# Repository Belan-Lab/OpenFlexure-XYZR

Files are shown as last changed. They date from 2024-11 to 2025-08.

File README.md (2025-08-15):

Stand With Ukraine (https://stand-with-ukraine.pp.ua)

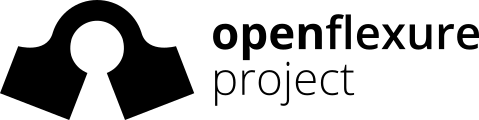
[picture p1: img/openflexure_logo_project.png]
OpenFlexure Project (https://gitlab.com/openflexure)


OpenFlexure Block Stage for SPIM
============================

Fork of [OpenFlexure Block Stage](https://gitlab.com/openflexure/openflexure-block-stage/) project.

Modification of the original Block Stage for SPIM imaging.

Department of Molecular Biophysics, Bogomoletz Institute of Physiology of NAS of Ukraine (Kyiv, Ukraine).

---

# Setup overview

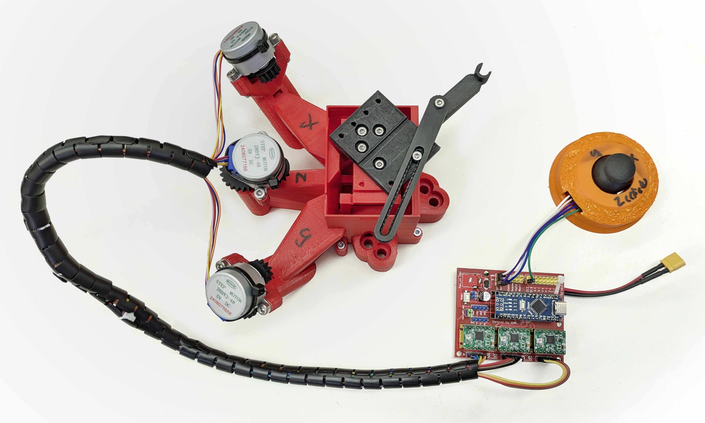
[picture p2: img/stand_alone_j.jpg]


Part|#|Cost/unit|Link
-|-|-|-
OpenFlexure Block Stage | 1x | $11 |-
Arduino Nano compatible board | 1x | $2.13 | [AliExpress](https://a.aliexpress.com/_EwrjzyD) 
Arduino Nano CNC board | 1x | $2.8 | [arduino.ua](https://arduino.ua/prod1745-modyl-3d-printera-v-3-0) 
Stepper driver A4988 | 3x | $1.3 | [arduino.ua](https://arduino.ua/prod965-draiver-shagovogo-dvigatelya-stepstick-a4988) 
Stepper drive 28BYJ-48, 5V | 3x | $1.45 | [arduino.ua](https://arduino.ua/prod216-shagovii-dvigatel-5v-28byj-48) 
Joystick module | 1x | $0.75 | [arduino.ua](https://arduino.ua/prod194-djoistik-dlya-arduino) 
Mini560 Pro Step Down to 5V | 1x | $0.85 | [AliExpress](https://a.aliexpress.com/_EJQFP5x) 
XT30 connector | 1x | $0.6 | [arduino.ua](https://arduino.ua/prod5276-xt30-konnektor-para-dlya-podklucheniya-li-po-li-ion-akkymylyatorov) 
30 cm Dupont jumpers kit | 1x | $0.95 | [arduino.ua](https://arduino.ua/prod2334-pepermichki-mama-papa-300mm) 
10 mm Spiral cable organizer | 1x | $2.60 | [AliExpress](https://a.aliexpress.com/_EIXyu5w) 
__Total__ |  | __~$30__ |

# Travel distances enlargement
## Modification V0
The original OpenFlexure Block stage has only ~2 mm travel distances in each direction, which is not enough for large sample imaging. So, due to the parametric nature of the OpenFlexure Block Stage model, I just adjusted several variables in the `parameters.scad` file to obtain an STL model of the stage with enlarged travel distances.  Additionally, I established a new variable `platform_z_add` which was just a constant in `platform_z` calculation (line 80) to control base high.

I am listing the changed parameters below:

| Variable               | Original value | Adjusted value |
| ---------------------- | -------------- | -------------- |
| `beam_height`          | 75             | 100            |
| `stage_to_beam_height` | 12.5           | 0              |
| `xy_lever`             | 10             | 30             |
| `flex_a`               | 0.1            | 0.2            |
| `platform_z_add`       | 7              | 20             |

Sample movement parameters:
- `xy_reduction`=  50 / `xy_lever` = 50/30 = 1.6
- `z_reducion` =  50 / `z_lever` = 50/10 = 5
- M3 screw pitch 0.5 mm

With selected parameters, we achieve next characteristics:

| Axis | Travel distance | Travel per screw revolution (estimated) |
| ---- | --------------- | --------------------------------------- |
| X    | ~6 mm           | 0.313 mm                                |
| Y    | ~6 mm           | 0.313 mm                                |
| Z    | ~3 mm           | 0.1 mm                                  |

__Materials:__

| Part                 | #      | Cost/unit | Link                                                         |
| -------------------- | ------ | --------- | ------------------------------------------------------------ |
| 1.75 mm PLA filament | ~200 g | ~$4.75    | [Monofilament](https://monofilament.com.ua/ua/products/standartnye-materialy/pla/pla-cvetlo-seryj-o1-75mm-ves0-75kg) |
| Silicone O-ring kit  | 1x     | $4.05     | [AliExpress](https://a.aliexpress.com/_EQdsBUy)              |
| 35 mm M3 screw       | 3x     | ~$0.5     | Metalvis                                                     |
| M3 nut               | 6x     | ~$0.25    | Metalvis                                                     |
| __Total__            |        | __~$11__  |                                                              |

# Setup configurations
## Stand-alone joystick control
Simple single speed stage control with joystick, sketch `arduino/cnc_board_joystick_xyz.ino`. Stage works in two modes, XY movement and Z movement, switching between them with joystick click button.

Stepper speed set up at 15 RPM, which achiwed travel speed 0.08 mm/s for XY axes and 0.025 mm/s for Z axis. Minimum rotation value set at 10 degrees per joystick activation. 

Estimated movement parameters:
- ~9 um per joystick activation for XY axes 
- ~3 um per joystick activation for Z axis

[Joystick module case](https://www.printables.com/model/653949-joystick-module-case) model avaliables on Printables (© @ZbychuM_510985).

## μManager control
3-axis stage control with [MarzhauserLStep](https://micro-manager.org/MarzhauserLStep) device adapter, Inspired by [CustomArduino](https://micro-manager.org/CustomArduino) vLStep Z-Axis solution.

# Hardware modifications
## Simple sample holder
Good practice for sample fixation during SPIM imaging is embedding the sample in agarose gel. 1 ml syringes are very suitable for large samples, so I designed a "lego figure hand"-like holder for a standard 1 ml insulin syringe. 

> [!TIP]
>
> Read about [sample preparation for SPIM](https://openspim.org/Sample_Preparation).

 Sample holder model V0 | Block Stage top view   | Block Stage side view 
:-------------------------:|:-------------------------:|:-------------------------:
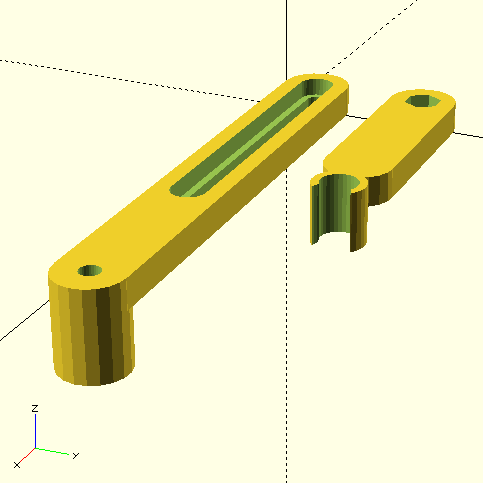
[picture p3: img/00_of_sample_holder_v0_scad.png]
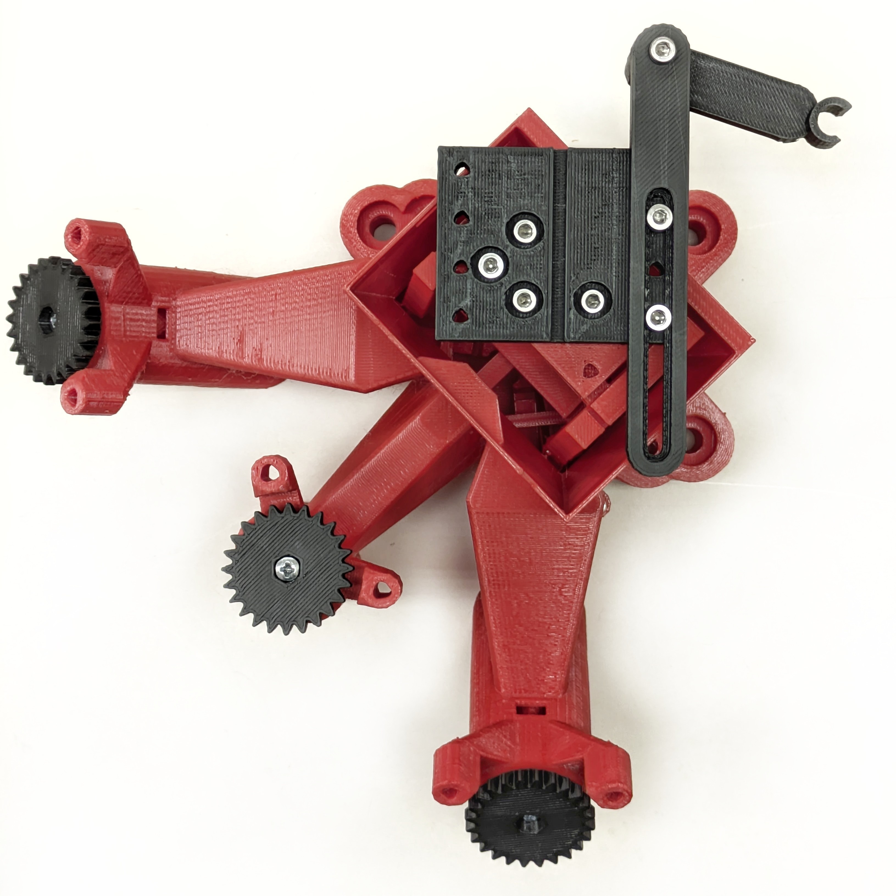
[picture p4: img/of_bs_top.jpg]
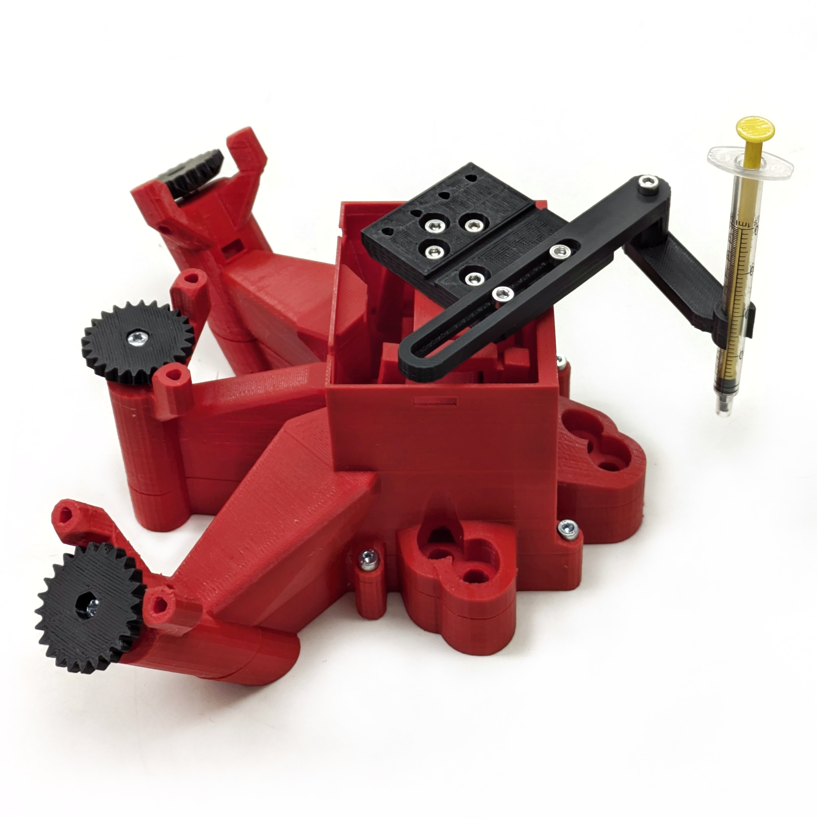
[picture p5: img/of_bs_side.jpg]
||

## R-axis arm
Moving platform modification with additional rotary axis.

_in progress_

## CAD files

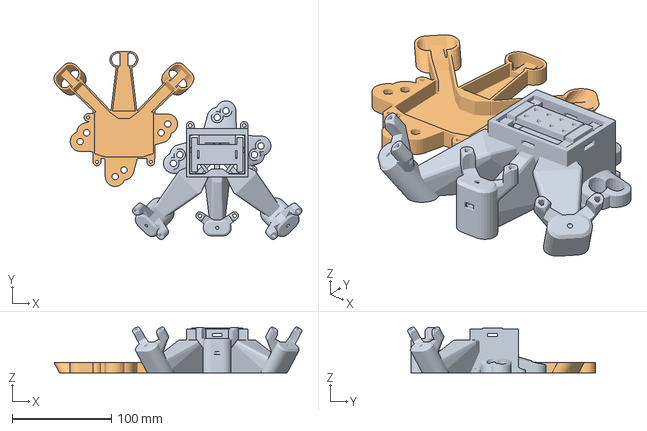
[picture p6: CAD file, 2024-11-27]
models/block_stage_large/K1/main_body_00.3mf
249.4 x 188.9 x 46.1 mm
main_body.stl
base.stl

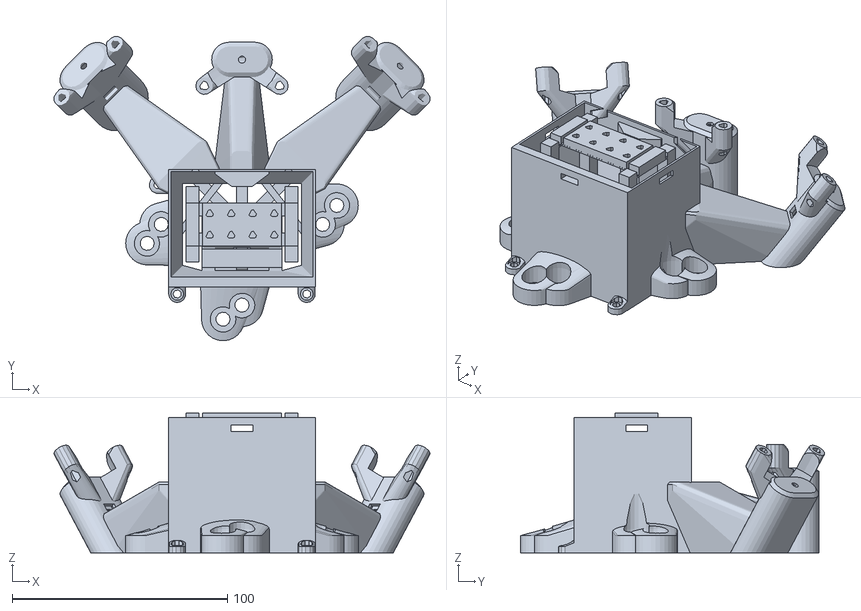
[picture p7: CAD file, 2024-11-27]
models/block_stage_large/builds/main_body.stl
174.8 x 141.4 x 65.0

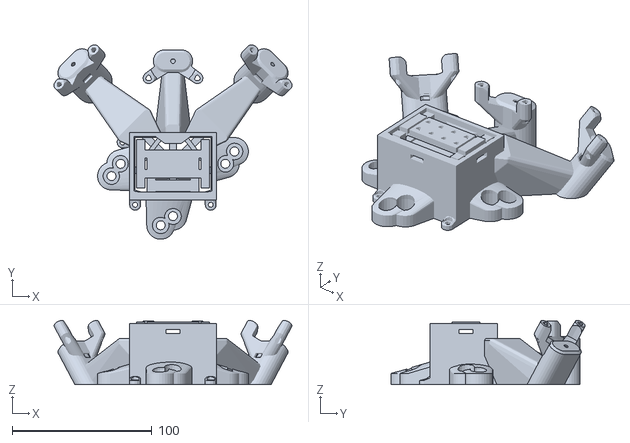
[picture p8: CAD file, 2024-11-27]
models/block_stage_original/builds/main_body.stl
170.5 x 139.3 x 46.1

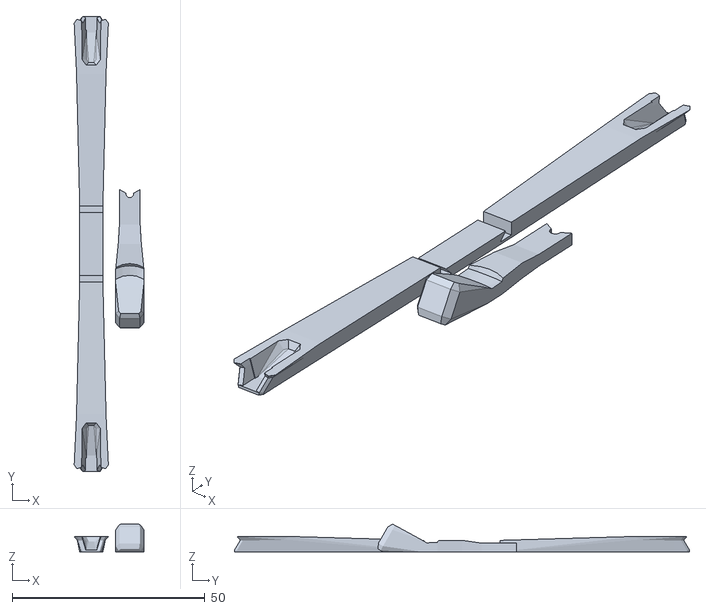
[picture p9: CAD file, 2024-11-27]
models/block_stage_original/builds/actuator_assembly_tools.stl
18.1 x 118.2 x 7.23

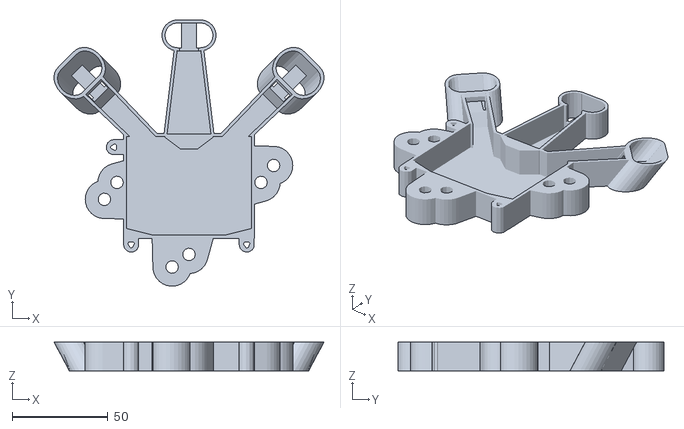
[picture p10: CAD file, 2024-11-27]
models/block_stage_large/builds/base.stl
140.6 x 138.7 x 15.0

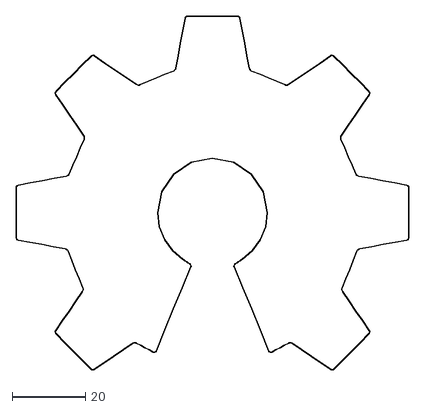
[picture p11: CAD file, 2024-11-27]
models/block_stage_large/openscad/oshw_gear.dxf
107.1 x 96.4

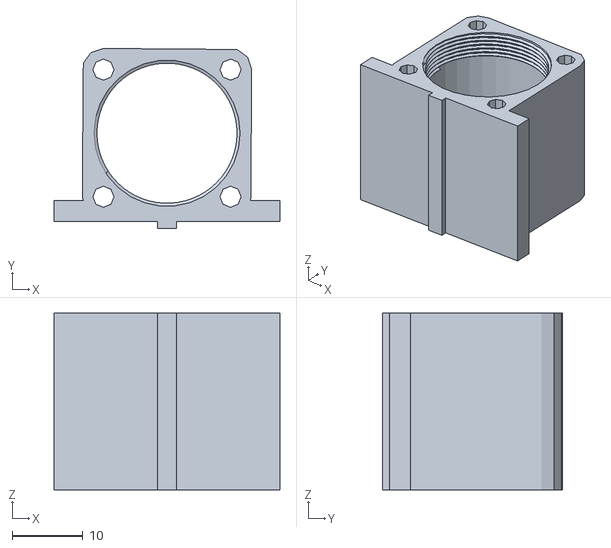
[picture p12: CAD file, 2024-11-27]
models/block_stage_original/builds/accessories/rms_to_top_plate.stl
32.0 x 25.5 x 25.0

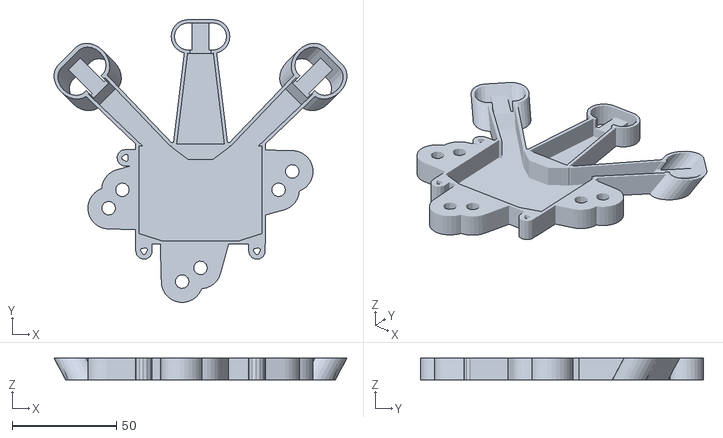
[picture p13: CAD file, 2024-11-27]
models/block_stage_original/builds/base.stl
140.6 x 135.7 x 10.5

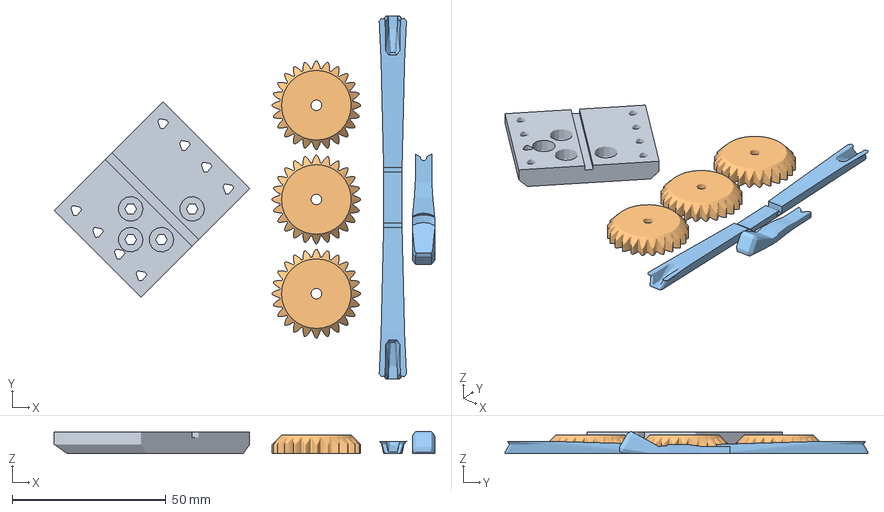
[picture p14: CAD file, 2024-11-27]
models/block_stage_large/K1/moving_platform_00.3mf
123.9 x 118.2 x 7.23 mm
moving_platform.stl
gears.stl
actuator_assembly_tools.stl

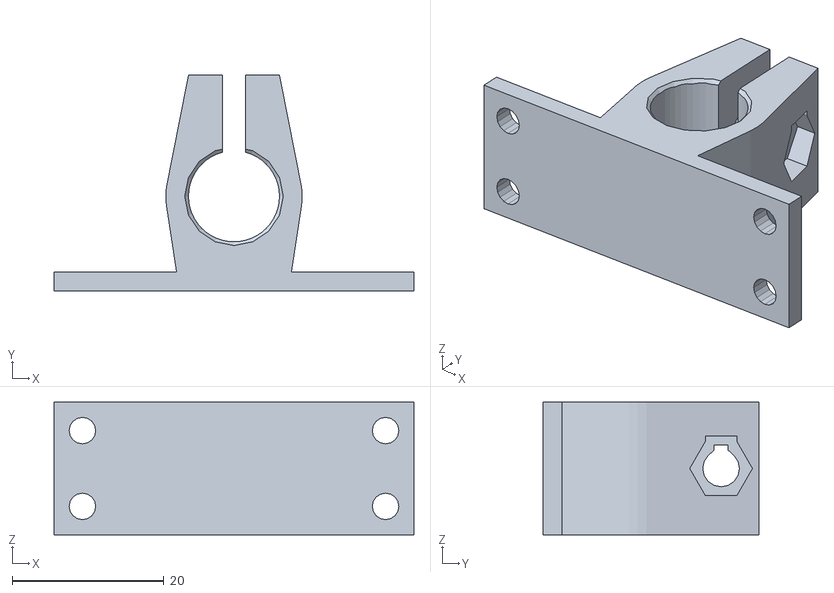
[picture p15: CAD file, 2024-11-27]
models/block_stage_original/builds/accessories/CPS532_to_top_plate.stl
47.5 x 28.5 x 17.5

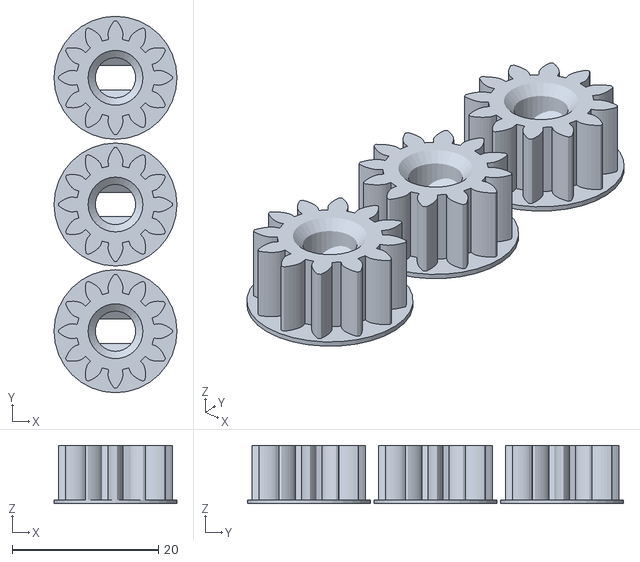
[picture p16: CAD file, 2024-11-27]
models/block_stage_original/builds/small_gears.stl
16.8 x 51.5 x 8.00

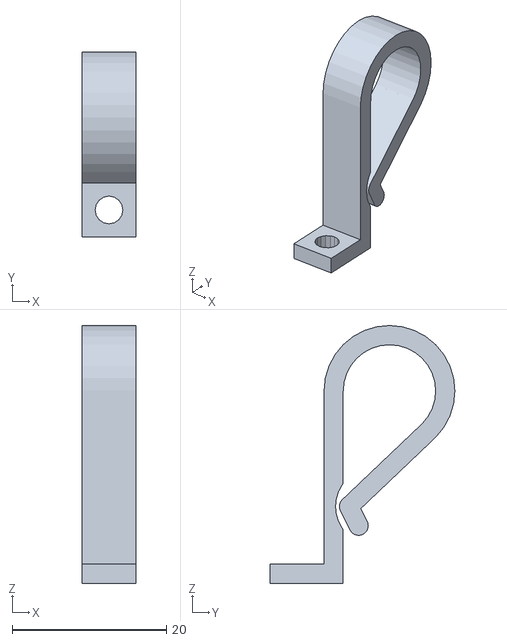
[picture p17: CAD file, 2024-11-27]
models/block_stage_original/builds/accessories/vertical_sample_clips.stl
7.00 x 24.0 x 33.5

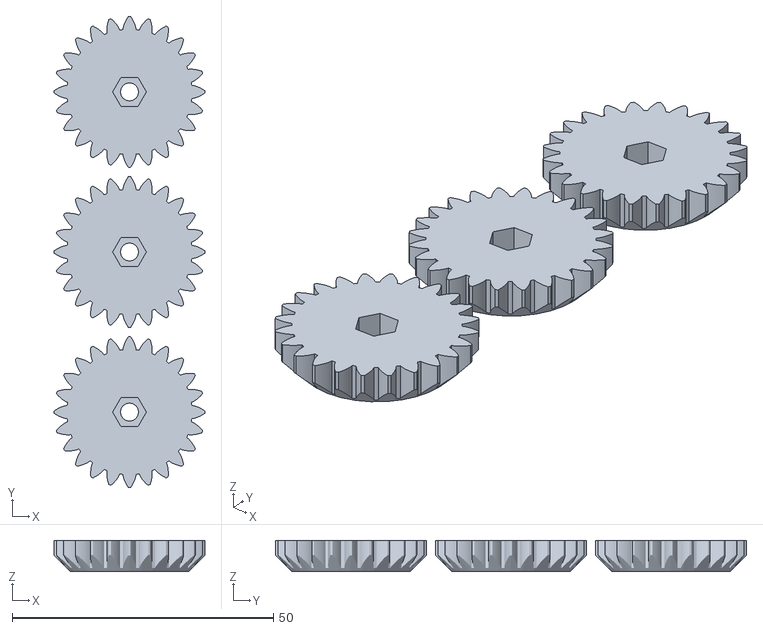
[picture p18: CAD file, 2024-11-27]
models/block_stage_original/builds/gears.stl
28.9 x 90.2 x 6.00

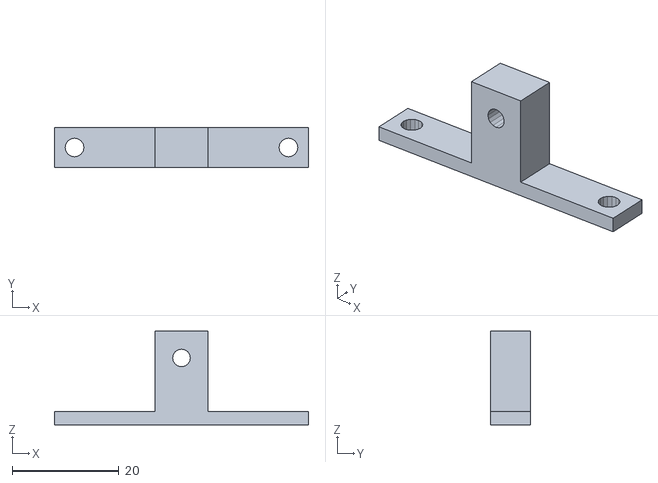
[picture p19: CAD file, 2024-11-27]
models/block_stage_original/builds/accessories/LED_to_top_plate.stl
47.5 x 7.50 x 17.5

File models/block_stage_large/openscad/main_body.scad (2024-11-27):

use <utilities.scad>;
use <compact_nut_seat.scad>;
use <fibre_stage_three_legs.scad>;
include <parameters.scad>;

module exterior_brim(r=4, h=0.2){
    // Add a "brim" around the outside of an object *only*, preserving holes in the object
    children();
    
    if(r>0) linear_extrude(h) difference(){
        offset(r) projection(cut=true) translate([0,0,-d]) children();
       
        offset(-r) offset(r) projection(cut=true) translate([0,0,-d]) children();
    }
}
module z_base(){
    // Trapezoid that forms the base of the Z stage
    t = xy_bottom_travel;
    w = z_stage_base_w;
    hull(){
        translate([-pw,-pw-t,0]) cube([2*pw,d,d]); // inner edge
        translate([-w/2, -stage[1]/2-t, 0]) cube([w, d, d]);
        translate([-w/2, z_stage_base_y, 0]) cube([w, d, d]);
    }
}

module z_stage(){
    // This is the part that moves in Z only, connected to the middle
    // "shelf" of the XY table
    // The triangular base of this part must fit between the 
    // pushsticks for the XY motion, which constrains the tip position
    // and also means we must bring the sides out at 45 degrees.
    difference(){
        sequential_hull(){
            z_base();
            translate([0,0,stage[2]]) z_base();
            translate([0,0,shelf_z1 + stage[2]/2]) cube(stage,center=true);
        }
        
        // clearance for Z pushstick (see below)
        translate([-pw/2-1.5, -99, z_pushstick_z - 2 - z_travel]){
            cube([pw+3, 999, pushstick[2]+3.5+2*z_travel]);
        }
    }
    // Join the stage to the anchor with some flexures at the bottom
    reflect([1,0,0]) translate([-z_stage_base_w/2,z_anchor_bottom_y-d,0])
        cube([zflex[0], z_lever + zflex[1]+2*d, zflex[2]]);
    translate([-z_stage_base_w/2,z_anchor_bottom_y+zflex[1],0])
        cube([z_stage_base_w, z_lever - zflex[1], pushstick[2]]);
    // And more flexures at the top
    reflect([1,0,0]) translate([-stage[0]/2,-stage[1]/2,shelf_z1]) mirror([0,1,0]){
        translate([0,-d,0]) cube([zflex[0], z_lever + zflex[1]+2*d, zflex[2]]);
        translate([0,zflex[1],dz]) cube([stage[0]/2+d,z_lever - zflex[1], stage[2]-dz]);
    }
    // The actuating "pushstick" attaches to this lever
    hull(){
        translate([-pw/2, z_stage_base_y - z_lever, 0]) cube([pw, z_lever - zflex[1], stage[2]]);
        translate([-pw/2, z_stage_base_y - 3 - zflex[1], 0]) cube([pw, 3, shelf_z1 - 3]);
    }
    // This is the actuating "pushstick"
    translate([-pw/2, z_stage_base_y, z_pushstick_z]){
        l = z_actuator_pivot_y - z_stage_base_y;
        cube([pw, l, pushstick[2]]);
        translate([0,-zflex[1]*2,0]) cube([pw, l + 4*zflex[1], zflex[2]]);
    }
}

// Overall structure
module main_body(){
    difference(){
        xy_table();
        
        // cutouts for pushsticks
        each_pushstick() hull() {
            h=stage[2]*2+z_travel*2;
            translate([0,2*d,0]) cube([pw, d, h], center=true);
            translate([0,0.5,0]) cube([pw+1.5, d, h], center=true);
            translate([0, pushstick[1], 0]) cube([pw+1+2*xy_bottom_travel*sqrt(2), d, h], center=true);
            translate([0, pushstick[1], 0]) cube([d, d, h + pw+1+2*xy_bottom_travel*sqrt(2)], center=true);
            translate([99, 98, 0]) cube([d, d, h + pw+1+2*xy_bottom_travel*sqrt(2)], center=true); //cut out between the pushsticks
        }
        
        // cutout for Z stage
        hull(){
            h=stage[2]*2+z_travel*2;
            w = stage[0] - 2*zflex[1];
            translate([0, -pw, 0]) cube([2*pw,d,h],center=true);
            translate([0, -stage[1]/2, 0]) cube([w,2*d,h],center=true);
        }
        
        // mounting holes on top
        repeat([10,0,0],4,center=true)
            repeat([0,10,0],2,center=true)
            translate([0,0,shelf_z2 + 1.5]) trylinder_selftap(3,h=999);
            // NB the z position must clear the bottom of the stage
            // (which is 1mm above shelf_z2) or we get errors on the
            // bridge.
    }
    // XY pushsticks and actuators
    each_pushstick(){
        pushstick();
        translate([0,pushstick[1] - zflex[1],0]) tilted_actuator(shelf_z1, xy_actuator_pivot_w, xy_lever * xy_reduction, base_w = pw);
    }
    
    // Z stage (the part that moves only in Z) and actuator
    z_stage();
    translate([0,z_actuator_pivot_y,0]){
        untilted_actuator(z_pushstick_z, z_actuator_pivot_w, z_lever * z_reduction);
    }
    //reinforcement through the void in the centre
    reflect([1,0,0]) translate([0,0,pushstick[2] + 4 + z_travel]) hull(){
        translate([pw/2+3, z_actuator_pivot_y - wall_t, 0]) cube([4,d,4]);
        translate([stage[0]/2 + zflex[0] + zflex[1] + xy_bottom_travel, -stage[1]/2,0]) cube([0.5,4,4]);
    }
    
    // Casing (also provides a lot of the structural integrity)
    casing();
    // if(fixed_platform) fixed_platform(); <<<<<<<<<<<<<<<<<<
        
    
}//*/
brim_r=0;
exterior_brim(r=brim_r) main_body();

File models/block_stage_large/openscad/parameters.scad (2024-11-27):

/*
  Useful settings/parameters for the OpenFlexure fibre stage
*/
version_numstring = "0.2.1";
stage = [37,20,5]; // dimensions of stage part
beam_height = 100; // 75 <<<<<< height of beam above the table
stage_to_beam_height = 0; // 12.5 <<<<<<
stage_height = beam_height - stage_to_beam_height; //bottom of base to top surface of the stage 
 // NB platform_z sets the distance from bottom of the body to top of the stage
 // stage_height determines the thickness of the base.
platform_z_add = 20;

brim_r = 0;

// Range of travel is lever length * flex_a
xy_lever = 30;  // 10 <<<<<<<<<<<<<<<<<<<<<
z_lever = 10;   // 10 <<<<<<<<<<<<<<<<<<<<<

// Mechanical reduction settings
xy_stage_reduction = 30/xy_lever; //ratio of sample motion to lower shelf motion
xy_reduction = 50/xy_lever; //mechanical reduction from screw to sample
z_reduction = 50/z_lever; //mechanical reduction for Z

// Motor lugs
motor_lugs = true;

// fixed platform for fibre launch
//fixed_platform = false; // this is overwritten later on with the dimensions anyway.

// Mounting holes
breadboard_lugs="diagonal"; //sets the hole pattern for bolting it down.  See the options below.

// Flexure dimensions - good for PLA and ~0.5mm nozzle
zflex = [6, 1.5, 0.75]; //dimensions of flexure
xflex = [5,5.5,5]; //default bounding box of x flexure
xflex_t = 1; //thickness of bendy bit in x
flex_a = 0.2; //angle through which flexures are bent, radians, 0.1 <<<<<
dz = 0.5; //thickness before a bridge is printable-on

xy_travel = xy_lever * flex_a; //max. travel in X or Y
xy_bottom_travel = xy_travel * xy_stage_reduction; //travel of bottom of XY stage
xy_actuator_pivot_w = 25; //width of the hinge for the actuating lever
actuator_h = 26; //height of actuator columns (~screw length)

pushstick = [5,38,5]; //cross-section of XY "push stick"
pw = pushstick[0]; //because this is used in a lot of places...

wall_t = 1.6;
d=0.05;

// Height of the bridging "shelves" in the XY axis "table" structure
shelf_z1 = xy_lever * xy_stage_reduction;
shelf_z2 = shelf_z1 + xy_lever;

// Z axis geometry
z_travel = z_lever * flex_a; //max. travel in Z
z_stage_base_y = -stage[1]/2-xy_bottom_travel; //position of the flexure edge of the Z stage
z_stage_base_w = stage[0] + 2*zflex[1] - 2*xy_bottom_travel - 2; //width of the flexure edge of the Z stage
z_anchor_bottom_y = z_stage_base_y - z_lever - zflex[1]; // lower Z stage end of the fixed base
z_actuator_pivot_y = stage[1]/2 + zflex[1] + zflex[0] + xy_bottom_travel + wall_t;
z_actuator_pivot_w = 20; //width of the hinge for the Z actuator lever
z_pushstick_z = shelf_z1 - pw - 2.5; // height of the Z pushstick

// Mounting stuff
// By default, place 3 mounting holes to align the centre of the stage with a hole.
// setting beam_between_holes adds another set of holes, putting the beam halfway between
bolt_spacing = 25; // change to 25.4 for imperial tables
mounting_bolts_alongholes = [[-1,0,0],[0,-1,0],[1,0,0]]*1.5*bolt_spacing; //beam aligned with holes
mounting_bolts_betweenholes = [[-1.25,-0.25,0],[1.25,0.25,0],[-0.25,-1.25,0]]*1.41*bolt_spacing;
mounting_bolts_atsides = [[-1.5,0,0],[1.5,0,0],[-1.5,-1,0],[1.5,-1,0]] * bolt_spacing;
mounting_bolts_diagonal = concat(mounting_bolts_alongholes, 
                                 mounting_bolts_betweenholes);
// I hope you'll excuse the stacked ternaries, this is an unpleasant necessity :(
mounting_bolts = breadboard_lugs=="atsides"?mounting_bolts_sides:
                 breadboard_lugs=="diagonal"?mounting_bolts_diagonal:
                 breadboard_lugs=="alongholes"?mounting_bolts_alongholes:
                 breadboard_lugs=="betweenholes"?mounting_bolts_betweenholes:
                 /*breadboard_lugs=="none"?*/[];
            
platform_z = shelf_z2 + stage[2] + platform_z_add; // 7 <<<<<<< The platform is a fixed height above the moving stage
fixed_platform_standoff = 10;
fixed_platform = [50,40,4];
platform_gap = xy_travel + 1;

//term for calculating casing size
casing_size_s = xy_bottom_travel + zflex[1] + zflex[0] + 0.5 + wall_t;
//casing size
casing_size = stage + [2*casing_size_s,casing_size_s + (-z_anchor_bottom_y-stage[1]/2) + wall_t,shelf_z2];
casing_top = shelf_z2 + stage[2] - z_travel; // top of the wall
max_actuator_travel = max(xy_travel*xy_reduction, z_travel*z_reduction); // maximum distance the actuators protrude below the stage
echo(max_actuator_travel);

base_height = stage_height - platform_z; // the base takes up any height not use by the body.
if(base_height < max_actuator_travel + 4) echo("WARNING: stage_height is too low, base will not compile properly!");

//foot_height is required for the actuator assembly tools
foot_height = 20;

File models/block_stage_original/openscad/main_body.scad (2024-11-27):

use <utilities.scad>;
use <compact_nut_seat.scad>;
use <fibre_stage_three_legs.scad>;
include <parameters.scad>;

module exterior_brim(r=4, h=0.2){
    // Add a "brim" around the outside of an object *only*, preserving holes in the object
    children();
    
    if(r>0) linear_extrude(h) difference(){
        offset(r) projection(cut=true) translate([0,0,-d]) children();
       
        offset(-r) offset(r) projection(cut=true) translate([0,0,-d]) children();
    }
}
module z_base(){
    // Trapezoid that forms the base of the Z stage
    t = xy_bottom_travel;
    w = z_stage_base_w;
    hull(){
        translate([-pw,-pw-t,0]) cube([2*pw,d,d]); // inner edge
        translate([-w/2, -stage[1]/2-t, 0]) cube([w, d, d]);
        translate([-w/2, z_stage_base_y, 0]) cube([w, d, d]);
    }
}

module z_stage(){
    // This is the part that moves in Z only, connected to the middle
    // "shelf" of the XY table
    // The triangular base of this part must fit between the 
    // pushsticks for the XY motion, which constrains the tip position
    // and also means we must bring the sides out at 45 degrees.
    difference(){
        sequential_hull(){
            z_base();
            translate([0,0,stage[2]]) z_base();
            translate([0,0,shelf_z1 + stage[2]/2]) cube(stage,center=true);
        }
        
        // clearance for Z pushstick (see below)
        translate([-pw/2-1.5, -99, z_pushstick_z - 2 - z_travel]){
            cube([pw+3, 999, pushstick[2]+3.5+2*z_travel]);
        }
    }
    // Join the stage to the anchor with some flexures at the bottom
    reflect([1,0,0]) translate([-z_stage_base_w/2,z_anchor_bottom_y-d,0])
        cube([zflex[0], z_lever + zflex[1]+2*d, zflex[2]]);
    translate([-z_stage_base_w/2,z_anchor_bottom_y+zflex[1],0])
        cube([z_stage_base_w, z_lever - zflex[1], pushstick[2]]);
    // And more flexures at the top
    reflect([1,0,0]) translate([-stage[0]/2,-stage[1]/2,shelf_z1]) mirror([0,1,0]){
        translate([0,-d,0]) cube([zflex[0], z_lever + zflex[1]+2*d, zflex[2]]);
        translate([0,zflex[1],dz]) cube([stage[0]/2+d,z_lever - zflex[1], stage[2]-dz]);
    }
    // The actuating "pushstick" attaches to this lever
    hull(){
        translate([-pw/2, z_stage_base_y - z_lever, 0]) cube([pw, z_lever - zflex[1], stage[2]]);
        translate([-pw/2, z_stage_base_y - 3 - zflex[1], 0]) cube([pw, 3, shelf_z1 - 3]);
    }
    // This is the actuating "pushstick"
    translate([-pw/2, z_stage_base_y, z_pushstick_z]){
        l = z_actuator_pivot_y - z_stage_base_y;
        cube([pw, l, pushstick[2]]);
        translate([0,-zflex[1]*2,0]) cube([pw, l + 4*zflex[1], zflex[2]]);
    }
}

// Overall structure
module main_body(){
    difference(){
        xy_table();
        
        // cutouts for pushsticks
        each_pushstick() hull() {
            h=stage[2]*2+z_travel*2;
            translate([0,2*d,0]) cube([pw, d, h], center=true);
            translate([0,0.5,0]) cube([pw+1.5, d, h], center=true);
            translate([0, pushstick[1], 0]) cube([pw+1+2*xy_bottom_travel*sqrt(2), d, h], center=true);
            translate([0, pushstick[1], 0]) cube([d, d, h + pw+1+2*xy_bottom_travel*sqrt(2)], center=true);
            translate([99, 98, 0]) cube([d, d, h + pw+1+2*xy_bottom_travel*sqrt(2)], center=true); //cut out between the pushsticks
        }
        
        // cutout for Z stage
        hull(){
            h=stage[2]*2+z_travel*2;
            w = stage[0] - 2*zflex[1];
            translate([0, -pw, 0]) cube([2*pw,d,h],center=true);
            translate([0, -stage[1]/2, 0]) cube([w,2*d,h],center=true);
        }
        
        // mounting holes on top
        repeat([10,0,0],4,center=true)
            repeat([0,10,0],2,center=true)
            translate([0,0,shelf_z2 + 1.5]) trylinder_selftap(3,h=999);
            // NB the z position must clear the bottom of the stage
            // (which is 1mm above shelf_z2) or we get errors on the
            // bridge.
    }
    // XY pushsticks and actuators
    each_pushstick(){
        pushstick();
        translate([0,pushstick[1] - zflex[1],0]) tilted_actuator(shelf_z1, xy_actuator_pivot_w, xy_lever * xy_reduction, base_w = pw);
    }
    
    // Z stage (the part that moves only in Z) and actuator
    z_stage();
    translate([0,z_actuator_pivot_y,0]){
        untilted_actuator(z_pushstick_z, z_actuator_pivot_w, z_lever * z_reduction);
    }
    //reinforcement through the void in the centre
    reflect([1,0,0]) translate([0,0,pushstick[2] + 4 + z_travel]) hull(){
        translate([pw/2+3, z_actuator_pivot_y - wall_t, 0]) cube([4,d,4]);
        translate([stage[0]/2 + zflex[0] + zflex[1] + xy_bottom_travel, -stage[1]/2,0]) cube([0.5,4,4]);
    }
    
    // Casing (also provides a lot of the structural integrity)
    casing();
    // if(fixed_platform) fixed_platform(); <<<<<<<<<<<<<<<<<<
        
    
}//*/
brim_r=0;
exterior_brim(r=brim_r) main_body();

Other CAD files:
models/block_stage_original/builds/moving_platform.stl
models/block_stage_original/openscad/parameters.scad
models/block_stage_large/openscad/accessories/CPS532_to_top_plate.scad
models/block_stage_large/openscad/accessories/LED_to_top_plate.scad
models/block_stage_large/openscad/accessories/cylinder_clamp.scad
models/block_stage_large/openscad/accessories/microscope_module.scad
models/block_stage_large/openscad/accessories/microscope_module_infiniteconjugates.scad
models/block_stage_large/openscad/accessories/optics_module_rms_f50d13_nodovetail.scad
models/block_stage_large/openscad/accessories/optics_mounts.scad
models/block_stage_large/openscad/accessories/picamera_shim.scad
models/block_stage_large/openscad/accessories/rms_to_top_plate.scad
models/block_stage_large/openscad/accessories/thorlabs_threads.scad
models/block_stage_large/openscad/accessories/vertical_sample_clips.scad
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

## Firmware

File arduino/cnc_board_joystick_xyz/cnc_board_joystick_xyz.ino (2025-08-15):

// Nano CNC board with stepper lib and joystick control

// #include "A4988.h"
#include <Arduino.h>
#include "BasicStepperDriver.h"
#include "MultiDriver.h"
#include "SyncDriver.h"

// joystick set up
#define X_STICK A7
#define Y_STICK A6
#define J_CLICK 12

#define U_LIM 614
#define D_LIM 414

int xPos = 0;
int yPos = 0;
int bStt = 0;
int bSttLast = 0;
int bPress = 0;

// steppers set up
#define X_DIR 2          // X-axis dir pin   X-2, Y-3. Z-4 
#define X_STEP 5         // X-axis step pin  X-5, Y-6. Z-7 


#define Y_DIR 3          // y-axis dir pin   X-2, Y-3. Z-4 
#define Y_STEP 6         // Y-axis step pin  X-5, Y-6. Z-7 


#define Z_DIR 4          // z-axis dir pin   X-2, Y-3. Z-4 
#define Z_STEP 7         // Z-axis step pin  X-5, Y-6. Z-7 


#define MOTOR_EN 8       // drivers enable pin

#define MOTOR_STEPS 2047  // steps per revolution

BasicStepperDriver stepperX(MOTOR_STEPS, X_DIR, X_STEP);
BasicStepperDriver stepperY(MOTOR_STEPS, Y_DIR, Y_STEP);
BasicStepperDriver stepperZ(MOTOR_STEPS, Z_DIR, Z_STEP);

SyncDriver controller(stepperX, stepperY, stepperZ);

int rotate = 360;


void setup() {
  // initialize serial communications at 9600 bps:
  Serial.begin(9600); 
  
  pinMode(X_STICK, INPUT);
  pinMode(Y_STICK, INPUT);
  pinMode(J_CLICK, INPUT_PULLUP);

  pinMode(MOTOR_EN, OUTPUT);
  digitalWrite(MOTOR_EN, LOW);

  stepperX.begin(15., 1);
  stepperY.begin(15., 1);
  stepperZ.begin(15., 1);

  pinMode(MOTOR_EN, OUTPUT);
  digitalWrite(MOTOR_EN, HIGH);

}


void loop() {
  bState();

  xPos = analogRead(X_STICK);
  yPos = analogRead(Y_STICK);
  
  if (bPress == 0){
    xyMove();
  }
  else if (bPress == 1){
    zMove();
  }

  Serial.print("X: ");
  Serial.print(xPos);
  Serial.print(" | Y: ");
  Serial.print(yPos);
  Serial.print(" | Button: ");
  Serial.println(bPress);
}


void xyMove() {
  if ((xPos > U_LIM) && (yPos > U_LIM)){
    digitalWrite(MOTOR_EN, LOW);
    delayMicroseconds(10);
    controller.rotate(-10, 10, 0);
    }
  else if ((xPos < D_LIM) && (yPos < D_LIM)){
    digitalWrite(MOTOR_EN, LOW);
    delayMicroseconds(10);
    controller.rotate(10, -10, 0);
    }
  else if ((xPos < D_LIM) && (yPos > U_LIM)){
    digitalWrite(MOTOR_EN, LOW);
    delayMicroseconds(10);
    controller.rotate(10, 10, 0);
    }
  else if ((xPos > U_LIM) && (yPos < D_LIM)){
    digitalWrite(MOTOR_EN, LOW);
    delayMicroseconds(10);
    controller.rotate(-10, -10, 0);
    }
  else if (yPos < D_LIM){
    digitalWrite(MOTOR_EN, LOW);
    delayMicroseconds(10);
    controller.rotate(0, -10, 0);
    }
  else if (yPos > U_LIM){
    digitalWrite(MOTOR_EN, LOW);
    delayMicroseconds(10);
    controller.rotate(0, 10, 0);
    }
  else if (xPos < D_LIM){
    digitalWrite(MOTOR_EN, LOW);
    delayMicroseconds(10);
    controller.rotate(10, 0, 0);
    }
  else if (xPos > U_LIM){
    digitalWrite(MOTOR_EN, LOW);
    delayMicroseconds(10);
    controller.rotate(-10, 0, 0);
    }
}


void zMove() {
  if (yPos < D_LIM){
    digitalWrite(MOTOR_EN, LOW);
    delayMicroseconds(10);
    controller.rotate(0, 0, 10);
    }
  else if (yPos > U_LIM){
    digitalWrite(MOTOR_EN, LOW);
    delayMicroseconds(10);
    controller.rotate(0, 0, -10);
    }
}


void bState() {
  int bStt = digitalRead(J_CLICK);

  if (bStt == LOW && bSttLast == HIGH) {
    bPress = !bPress;
  }

  bSttLast = bStt;
}

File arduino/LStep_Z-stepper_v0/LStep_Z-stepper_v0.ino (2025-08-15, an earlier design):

// Modified Arduino firmware for A4988 stepper and Micro-Manager compatibility
// Non-blocking stepper control with proper status reporting
// Stand-alone stepper control

// Motor configuration
#define MOTOR_STEPS 200     // Steps per revolution
#define MICROSTEPS 1        // Microstepping

// Pin definitions for A4988
#define DIR_PIN 4
#define STEP_PIN 7
#define ENABLE_PIN 8

String cmd = "";
float z = 0.0;
long stepPosition = 0;        // Current position in steps
float stepsPerUnit = 100.0;   // Steps per micrometer (adjust for your setup)

// Non-blocking movement variables
bool isMoving = false;
long moveStepsRemaining = 0;
int moveDirection = 1;
unsigned long lastStepTime = 0;
unsigned long stepIntervalMicros = 5000; // Default: 200 steps/sec

void setup() {
  Serial.begin(9600);
  
  // Configure stepper pins
  pinMode(DIR_PIN, OUTPUT);
  pinMode(STEP_PIN, OUTPUT);
  pinMode(ENABLE_PIN, OUTPUT);
  digitalWrite(ENABLE_PIN, LOW); // Enable motor (LOW = enabled for A4988)
  
  delay(1000);
  
  reply("Vers:LS");
}

void loop() {
  // Handle serial commands - HIGHEST PRIORITY
  if (Serial.available()) {
    cmd = Serial.readStringUntil('\r');
    processCommand(cmd);
    cmd = "";
  }

  // Non-blocking stepper movement
  handleStepperMovement();
}

void processCommand(String s) {
  if (s.startsWith("?ver")) {
    reply("Vers:LS");
  } else if (s.startsWith("!autostatus 0")) {
    // Just acknowledge
  } else if (s.startsWith("?det")) {
    reply("60");
  } else if (s.startsWith("?pitch z")) {
    reply("50.0");
  } else if (s.startsWith("?vel z")) {
    reply("100.0");
  } else if (s.startsWith("?accel z")) {
    reply("1.0");
  } else if (s.startsWith("!dim z 1")) {
    // Acknowledge dimension command
  } else if (s.startsWith("!dim z 2")) {
    // Acknowledge dimension command
  } else if (s.startsWith("?statusaxis")) {
    // CRITICAL: Return 'M' if moving, '@' if ready
    reply(isMoving ? "M" : "@");
  } else if (s.startsWith("!vel z")) {
    // Set velocity
    String speedStr = s.substring(s.indexOf('z') + 1);
    float speed = speedStr.toFloat();
    setMotorSpeed(speed);
  } else if (s.startsWith("!accel z")) {
    // Acknowledge acceleration command
  } else if (s.startsWith("?pos z")) {
    // Return current position
    String zs = String(z, 1);
    reply(zs);
  } else if (s.startsWith("?lim z")) {
    reply("0.0 100.0");
  } else if (s.startsWith("!pos z")) {
    // Set origin
    String posStr = s.substring(s.indexOf('z') + 1);
    if (posStr.length() > 0) {
      z = posStr.toFloat();
      stepPosition = (long)(z * stepsPerUnit);
    }
  } else if (s.startsWith("?status")) {
    reply("OK...");
  } else if (s.startsWith("!dim z 0")) {
    // Acknowledge dimension command
  } else if (s.startsWith("!speed z")) {
    // Acknowledge speed command
  } else if (s.startsWith("!mor z")) {
    // Relative move - NON-BLOCKING
    String delta = s.substring(s.indexOf('z') + 1);
    float deltaZ = delta.toFloat();
    z += deltaZ;
    startMove(deltaZ);
    // Reply immediately - don't wait for movement to complete
  } else if (s.startsWith("!moa z")) {
    // Absolute move - NON-BLOCKING
    String apos = s.substring(s.indexOf('z') + 1);
    float targetZ = apos.toFloat();
    float deltaZ = targetZ - z;
    z = targetZ;
    startMove(deltaZ);
    // Reply immediately - don't wait for movement to complete
  } else if (s.startsWith("?err")) {
    reply("0");
  }
}

void reply(String s) {
  Serial.print(s);
  Serial.print("\r");
  Serial.flush(); // Ensure immediate transmission
}

void setMotorSpeed(float speed) {
  // Convert speed to step interval (microseconds)
  // Adjust this mapping based on your requirements
  float stepsPerSecond = constrain(speed, 10, 1000);
  stepIntervalMicros = (unsigned long)(1000000.0 / stepsPerSecond);
}

void startMove(float deltaZ) {
  long deltaSteps = (long)(deltaZ * stepsPerUnit);
  if (deltaSteps == 0) {
    return;
  }
  
  // Stop any current movement
  isMoving = true;
  moveDirection = (deltaSteps > 0) ? 1 : -1;
  moveStepsRemaining = abs(deltaSteps);
  lastStepTime = micros();
}

void handleStepperMovement() {
  if (!isMoving) return;
  
  unsigned long currentTime = micros();
  if (currentTime - lastStepTime >= stepIntervalMicros) {
    lastStepTime = currentTime;
    
    // Set direction
    digitalWrite(DIR_PIN, (moveDirection > 0) ? HIGH : LOW);
    
    // Step pulse
    digitalWrite(STEP_PIN, HIGH);
    delayMicroseconds(2); // Minimum pulse width for A4988
    digitalWrite(STEP_PIN, LOW);
    
    // Update position
    stepPosition += moveDirection;
    moveStepsRemaining--;
    
    // Check if movement complete
    if (moveStepsRemaining <= 0) {
      isMoving = false;
    }
  }
}

/*
Command reference:
"?ver"   ->   Vers:LS
"?det"   ->   60  (device type)
"?statusaxis" -> @ if ready, M if busy
"!autostatus 0"
"?pitch z" -> 50.0
"!dim z 2" set to microns
"!dim z 1"
"?vel z"  -> 100.0
"!vel z 100" set velocity
"?accel z" -> 1.0
"!accel z 1" set acceleration
"!moa z 10"  move z to absolute position 10
"?err"  return 0
"!mor z 5" move z by relative amount 5
"?pos z" query current z position
"?lim z" query limits -> 0.0 100.0
"!pos z 0" set origin
"?status"  -> OK...
"!dim z 0" set as steps
"!speed z 10" set speed
*/

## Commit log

2024-11-27 27.11.2024: init commit
    [CPS532_to_top_plate.scad, CPS532_to_top_plate.stl, LED_to_top_plate.scad, LED_to_top_plate.stl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]
2025-08-15 15.08.2025: add Z stepper control with LStep
